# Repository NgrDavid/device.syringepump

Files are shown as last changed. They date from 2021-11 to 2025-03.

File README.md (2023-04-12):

## Harp Syringe Pump
This is a repository for the Harp Syringe Pump. The Harp Syringe Pump is a device that can be used to control the flow of liquid through a syringe by driving a stepper motor.
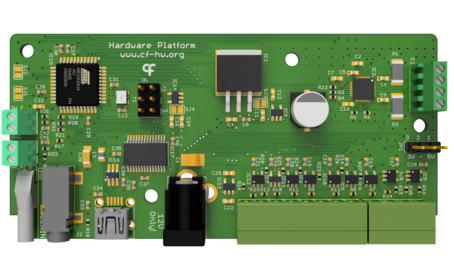
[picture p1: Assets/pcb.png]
HarpSyringePump


### Key Features ###

* Low and High-level interface control of the stepper motor
* General digital inputs configurable to trigger hardware events
* Digital outputs configurable to report hardware events
* Includes on-board stepper-motor driver
* Included mechanical designs and assembly instructions

### Connectivity ###

* 1x clock sync input (CLKIN) [stereo jack]
* 1x USB (for computer) [USB type B]
* 1x 12V supply [barrel connector jack]
* General purpose I/O (5V) [screw terminal]

## Interface ##

The interface with the Harp Behavior can be done through [Bonsai](https://bonsai-rx.org/) or a dedicated GUI (Graphical User Interface).

## Licensing ##

Each subdirectory will contain a license or, possibly, a set of licenses if it involves both hardware and software.

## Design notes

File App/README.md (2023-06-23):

# Syringe Pump GUI

This repository folder contains the Syringe Pump GUI (henceforth GUI) application that allows to configure the Syringe Pump device, developed by the Scientific Hardware Platform at the Champalimaud Foundation.

The Syringe Pump device is a Harp device and has all the inherent functionality of Harp devices.

The GUI was developed using [.NET 6](https://dotnet.microsoft.com/), [Avalonia](https://avaloniaui.net/) with ReactiveUI and makes direct use of the [Bonsai.Harp](https://github.com/bonsai-rx/harp) library.

As with other Harp devices, the Syringe Pump can also be used in [Bonsai](bonsai-rx.org/) using the [Bonsai.Harp.CF](https://github.com/bonsai-rx/harp.cf) package. 

## Installation

Go to the Releases page to download the latest version for your Operating System.

Currently there are x64 builds for Windows and Linux. Mac builds will be available in the future.

Portable builds are also available.

### Linux

Since the application accesses the serial port, your user needs to be on the `dialout`group or equivalent.

There might be other alternatives to this, but at least on Ubuntu and Fedora que command that you need to run to add your user to the `dialout` group is:

```sh
sudo usermod -a -G dialout <USERNAME>
```

## For developers

### Build Windows installer using NSIS manually

- Install NSIS 3 on your Windows machine
- Build and publish the application using the .NET 6 SDK command-line tools
  ```
    dotnet publish -r win-x64 /p:PublishSingleFile=false /p:IncludeNativeLibrariesInSingleFile=true /p:Configuration=Release
  ```
- Run makesis to generate the installer
    ```
     makensis.exe /DVERSION_MAJOR=0 /DVERSION_MINOR=1 /DVERSION_BUILD=0 .\SyringePump.nsi
    ```
- The installer will be available at `.\bin\Release\net6.0\win-x64\SyringePump.vx.x.x-win-x64.self-contained.exe`

### Build .app image for macOS

The project uses dotnet-bundle (https://github.com/egramtel/dotnet-bundle) to generate a .app image for macOS.

To build the .app image, run the following commands on the solution folder:

```sh
dotnet restore -r osx-x64 -p:TargetFramework=net6.0
dotnet msbuild -t:BundleApp -p:RuntimeIdentifier=osx-x64 -property:Configuration=Release -p:UseAppHost=true -p:TargetFramework=net6.0
```

### Build tar.gz package for Linux (either in Linux or WSL)

To build the tar.gz package, run the following commands on the solution folder:

First you need to make sure that the [`dotnet-packaging`](https://github.com/quamotion/dotnet-packaging) tool is installed

Run the following commands to install the tool:

```sh
dotnet tool install --global dotnet-tarball
```

Then run the following commands to build the tar.gz package:

```sh
dotnet restore -r linux-x64 -p:TargetFramework=net6.0
dotnet msbuild -p:RuntimeIdentifier=linux-x64 -property:Configuration=Release -p:UseAppHost=true -p:TargetFramework=net6.0 /t:CreateTarball
```

## Roadmap

See the [open issues](https://github.com/harp-tech/device.syringepump/issues) for a list of proposed features (and known issues).

## Contributing

Contributions are what make the open source community such an amazing place to be learn, inspire, and create. Any contributions you make are **greatly appreciated**.

1. Fork the Project
2. Create your Feature Branch (`git checkout -b feature/AmazingFeature`)
3. Commit your Changes (`git commit -m 'Add some AmazingFeature'`)
4. Push to the Branch (`git push origin feature/AmazingFeature`)
5. Open a Pull Request

## Authors

Hardware & Software Platform of the Champalimaud Foundation.

### Main contributors

- Artur Silva
- Luís Teixeira

## License

See `LICENSE` file for more information.

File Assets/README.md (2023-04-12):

### Licensing
Copyright harp-tech 2023

<br />This work is licensed under a <a rel="license" href="http://creativecommons.org/licenses/by/4.0/">Creative Commons Attribution 4.0 International License</a>.

#### You are free to:
*Share* — copy and redistribute the material in any medium or format.

*Adapt* — remix, transform, and build upon the material for any purpose, even commercially.

#### Under the following terms:
*Attribution* — You must give appropriate credit, provide a link to the license, and indicate if changes were made. You may do so in any reasonable manner, but not in any way that suggests the licensor endorses you or your use.

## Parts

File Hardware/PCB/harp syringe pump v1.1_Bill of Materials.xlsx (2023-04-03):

Part(s) | Quantity Low Level | Quantity Full | Description | Distributor | Part. No.
IC1 | 1 | 1 | Reguladores de tensão linear 3-TERMINAL POS REG 5V 1A | Mouser | 926-LM340S-5.0/NOPB | Low Level Only Bold
IC2 | 1 | 1 | DMOS Microstepping Driver with Translator and Overcurrent Protection IC | Farnell | 2057418
IC3, IC13, IC14 | 0 | 3 | LDO 250mA Ultra-Lo Noise LDO Reg | Mouser | 595-LP5907MFX-3.3NPB
IC4, IC5, IC6, IC7, IC10, IC11, IC12 | 0 | 7 | SingleBuffer / Driver, 1.65V to 5.5V, SOT-23-5 | Mouser | 595-SN74LVC1G125DBVR
IC8, IC9 | 0 | 2 | Buffers e line drivers 1.65-5.5V Single Non-Inverting TTL | Mouser | 863-M74VHC1GT50DTT1G
IC15 | 0 | 1 | Microcontroladores de 8 bits - MCU 44TQFP, IND TEMP GREEN, 1.6-3.6V | Mouser | 556-ATXMEGA128A4U-AU
IC16 | 0 | 1 | ESD Protection Low Cap | Mouser | 511-USBLC6-2SC6Y
IC17 | 0 | 1 | IC USB USB to Serial UART Enhanced IC SSOP-28 | Mouser | 895-FT232RL
C35, C36 | 0 | 2 | CAP CER 47pF 50V ±5% C0G 0402 | Mouser | 77-VJ0402A470JXACBC
C33 | 0 | 1 | CAP CER 4.7nF 100V ±10% X7R 0402 | Mouser | 81-GRM155R72A472KA01
C13, C14, C15, C16, C17, C18, C19, C20, C21, C22, C27, C28, C29, C34, C37, C39, C40, C41, C42 | 2 | 19 | CAP CER 100nF 10V ±10% X5R 0402 | Farnell | 2310530
C2, C5, C8 | 3 | 3 | CAP CER 100nF 100V ±10% X7R 0402 | Mouser | 81-GRM188R72A104KA35
C4, C7, C10 | 3 | 3 | CAP CER 220nF 100V ±10% X7R 0603 | Mouser | 81-GCM188R71H224KA4J
C30, C31 | 0 | 2 | CAP CER 330nF 10V ±10% X5R 0402 | Digikey | CL05A334KP5NNNC
C6, C9 | 2 | 2 | CAP CER 1uF 25V ±20% X5R 0603 | Mouser | 581-06033D105K
C38 | 0 | 1 | CAP TAN 4.7uF 10V ±10% 1206 | Mouser | 80-T491A475K107280
C11, C12, C23, C24, C25, C26, C32 | 1 | 7 | CAP CER 10uF 35V ±20% X5R 0603 | Mouser | 81-GRM188R6YA106MA3D
C1 | 1 | 1 | CAP TAN 22uF 20V ±10% 1210 | Mouser | 667-20TQC22MYFB
C3 | 1 | 1 | CAP ELE 100uF 25V ±20% | Mouser | 667-EEE-FK1E101P
R1, R2 | 2 | 2 | RES SMD 0.1Ω 1% 2010 1W | Mouser | 652-CRM2010FXR100ELF
R15, R16, R30, R31 | 2 | 4 | RES SMD 33Ω ±5% 0402 | Mouser | 667-ERJ-2GEJ330X
R34, R35 | 2 | 0 | RES SMD 33Ω ±5% 0402 | Mouser | 667-ERJ-2GEJ330X
R17 | 0 | 1 | RES SMD 68Ω 5% 0402 | Mouser | 71-CRCW0402-68-E3
R23, R24, R25, R26, R27, R28 | 6 | 0 | RES SMD 1kΩ 1% 0402 | Mouser | 667-ERJ-2RKF1001X
R19, R20, R21 | 0 | 3 | RES SMD 10kΩ 1% 0402 | Mouser | 667-ERJ-2RKF1002X
R32, R33 | 2 | 0 | RES SMD 10kΩ 1% 0402 | Mouser | 667-ERJ-2RKF1002X
R3 | 1 | 1 | RES SMD 24.9kΩ 1% 0402 | Mouser | 667-ERJ-2RKF2492X
R6 | 0 | 1 | RES SMD 39kΩ 1% 0402 | Mouser | 667-ERJ-2RKF3902X
R6 | 1 | 0 | RES SMD 36kΩ 1% 0402 | Mouser | 667-ERJ-2RKF3602X
R5 | 0 | 1 | RES SMD 54.9kΩ 1% 0402 | Mouser | 667-ERJ-U02F5492X
R5 | 1 | 0 | RES SMD 95.3kΩ 1% 0402 | Mouser | ERJ-U02F9532X
R4, R7, R8, R9, R10, R11, R12, R14, R22, R29 | 2 | 10 | RES SMD 100kΩ ±1% 0402 | Mouser | 667-ERJ-2RKF1003X
R18 | 0 | 1 | RES SMD 1MΩ 1% 0402 | Mouser | 652-CR0402FX-1004GLF
LED1 | 0 | 1 | LED, Green, 1.6mm x 0.8mm, 566 nm, 2.1 V, 20 mA, 15 mcd | Mouser | 78-TLMP1100-GS08
SW1 | 0 | 1 | Interruptores táteis 2.45N OF Long Stroke Green Button | Mouser | 653-B3AL-1001P
SW2 | 0 | 1 | Interruptores táteis 1.96N OF Long Stroke Red Button | Mouser | 653-B3AL-1000P
Y1 | 0 | 1 | 32MHz 10ppm | Mouser | 998-1001CI5032.0000T
J2 | 0 | 1 | SMT 3.5 STEREO REEL | Mouser | 502-35RASMT2BHNTRX
L1 | 0 | 1 | 40ohms 100MHz 1.5A Monolithic 0805 SMD | Mouser | 875-MI0805K400R-10
J3 | 0 | 1 | 6P DR UNSHRD HRD | Mouser | 649-67996-206HLF
X4 | 0 | 1 | UX60-MB-5S8 | Mouser | 798-UX60-MB-5S8
USB Cable | 0 | 1 | USB A - MINI-B 0.8M - MINI-B 0.8M BLACK | Mouser | 538-88732-8502
 | 0 | 1 | Tubos de Luz LED CML LIGHTPIPE | Mouser | 606-7513D2-L
JP1 | 0 | 1 | 3POS HDR 15AU | Mouser | 649-68001-203HLF
 | 0 | 1 | Distribuidores e Alojamento de Fios JUMPER SKT BLACK OPEN TOP | Mouser | 855-M7582-46
J1 | 1 | 1 | CC PCB 2.1MM | Mouser | 163-179PH-EX
SW_LIMITERS | 2 | 2 | SWITCH SNAP ACT SPST-NC 5A 125V | Mouser | 653-SS5GL22T
WALL ADAPTER | 1 | 1 | AC/DC Power Supply, Class II, Fixed, 1 Output, 90 V, 264 V, 12 W, 12 V | Farnell | VEL12US120-EU-JA
X1 | 1 | 1 | Wire-To-Board Terminal Block, 2.54 mm, 4 Ways, 30 AWG, 16 AWG, 1.4 mm², Screw | Farnell | 282834-4
 | 1 | 1 | 20.1550M/4-E - Pluggable Terminal Block, 3.5 mm, 4 Ways | Farnell | 2575217
 | 1 | 1 | 20.1550M/8-E - Pluggable Terminal Block, 3.5 mm, 8 Ways | Farnell | 2575220
X3 | 1 | 1 | Horizontal, Header, 3.5 mm, 4 Ways, 10 A, 250 V, Through Hole Right Angle | Farnell | 20.155MH/4-E
X2 | 1 | 1 | Horizontal, Header, 3.5 mm, 8 Ways, 10 A, 250 V, Through Hole Right Angle | Farnell | 20.155MH/8-E
 | 1 | 1 | Heat Sink, Black Anodised, 87 °C/W, For DIP, PLCC, SMD, 4.8mm/6.3mm/8mm | Farnell | 4302175
 | 1 | 1 | Thermal Conductive Foil, 0.37 W/m.K | Farnell | 1211706
 | 2 | 2 | Blocos de terminais fixos 2P SIDE ENTRY 2.54mm | Mouser | 571-282834-2
SJ1, SJ2, SJ3, SJ4 | 4 | 4 | - | - | -
Components | 51 | 112
PCB |  |  | 100mmx48mm 5x 2layers 35um
Licensed under the TAPR Open Hardware License (www.tapr.org/OHL)
Copyright 2020 Artur Silva, Champalimaud Foundation Scientific Hardware Platform

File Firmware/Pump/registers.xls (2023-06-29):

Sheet: registers
Has event. | When | Type | Array | Array Len. | Register Name | Description | Mask Type | Value | Name | Desciption
no |  | U8 | no |  | ENABLE_MOTOR_DRIVER | Enable the motor driver | bit | (1<<0) | MOTOR_ENABLE | Enable motor when equal to 1
no |  | U8 | no |  | START_PROTOCOL | Enable the defined protocol | bit | (1<<0) | START_PROTOCOL | Start the protocol when equal to 1
yes | Yes, when the register changes (either edge STEP changes) | U8 | no |  | STEP_STATE | Control the step of the motor controller | bit | (1<<0) | STEP_PIN | Status of the STEP motor controller pin
yes | Yes, when the register changes (either edge DIR changes) | U8 | no |  | DIR_STATE | Control the direction of the motor controller | bit | (1<<1) | DIR_PIN | Status of the DIR motor controller pin
yes | Yes, when the register changes (switch is triggered/cleared) | U8 | no |  | SW_FORWARD_STATE | State of the forward switch limit | bit | (1<<0) | SW_F_PIN | Status of the forward switch limit
yes | Yes, when the register changes (switch is triggered/cleared) | U8 | no |  | SW_REVERSE_STATE | State of the reverse switch limit | bit | (1<<1) | SW_R_PIN | Status of the reverse switch limit
yes | Everytime the pin changes the state | U8 | no |  | INPUT_STATE | Value of input 0 pin | bit | (1<<0) | DI0 | Input 0 value
no |  | U8 | no |  | SET_DOS | Set digital outputs | bit | (1<<0) | SET_DO0 | Write one to this bit will put digital out 0 into High state
 |  |  |  |  |  |  | bit | (1<<1) | SET_DO1 | Write one to this bit will put digital out 1 into High state
no |  | U8 | no |  | CLEAR_DOS | Clear digital outputs | bit | (1<<0) | CLR_DO0 | Write one to this bit will put digital out 0 into Low state
 |  |  |  |  |  |  | bit | (1<<1) | CLR_DO1 | Write one to this bit will put digital out 1 into Low state
no |  | U8 | no |  | DO0_CONFIG | Configures which signal is connected to the digital output 0 | mask | (3<<0) | OUT0_CONF | Select OUT0 function
 |  |  |  |  |  |  | group_mask | (0<<0) | OUT0_SOFTWARE | Digital output controlled by software
 |  |  |  |  |  |  | group_mask | (1<<0) | OUT0_SWLIMIT | Either limits reached (register SW_FORWARD_STATE OR SW_REVERSE_STATE)
no |  | U8 | no |  | DO1_CONFIG | Configures which signal is connected to the digital output 1 | mask | (3<<0) | OUT1_CONF | Select OUT1 function
 |  |  |  |  |  |  | group_mask | (0<<0) | OUT1_SOFTWARE | Digital output controlled by software (SET_DO1 and CLEAR_DO1)
 |  |  |  |  |  |  | group_mask | (1<<0) | OUT1_DATA_SEC | Toggles each second when is acquiring
 |  |  |  |  |  |  | group_mask | (2<<0) | OUT1_STEP_STATE | Equal to register STEP_STATE
no |  | U8 | no |  | DI0_CONFIG | Configuration of the digital input 0 (DI0) | mask | (3<<0) | DI0_CONF | Select IN0 function
 |  |  |  |  |  |  | group_mask | (0<<0) | DI0_SYNC | Use as a pure digital input
 |  |  |  |  |  |  | group_mask | (1<<0) | DI0_RISE_FALL_UPDATE_STEP | Update STEP with a rising edge
 |  |  |  |  |  |  | group_mask | (2<<0) | DI0_RISE_START_PROTOCOL | Will trigger the predefined protocol on a rising edge
no |  | U8 | no |  | MOTOR_MICROSTEP | Defines the motor microstep | mask | (7<<0) | MICROSTEP
 |  |  |  |  |  |  | group_mask | (0<<0) | STEP_FULL | Full step (2 phase)
 |  |  |  |  |  |  | group_mask | (1<<0) | STEP_HALF | Half step
 |  |  |  |  |  |  | group_mask | (2<<0) | STEP_QUARTER | Quarter step
 |  |  |  |  |  |  | group_mask | (3<<0) | STEP_EIGHTH | Eighth step
 |  |  |  |  |  |  | group_mask | (4<<0) | STEP_SIXTEENTH | Sixteenth step
no |  | U16 | no |  | PROTOCOL_NUMBER_STEPS | Number of steps [1;65535]
no |  | FLOAT | no |  | PROTOCOL_FLOWRATE | Flowrate value in uL/s ]0;max_float[
no |  | U16 | no |  | PROTOCOL_PERIOD | Period for each step in ms [1;65535]
no |  | FLOAT | no |  | PROTOCOL_VOLUME | Volume value in uL ]0;max_float[
no |  | U8 | no |  | PROTOCOL_TYPE | Step-based (0) or Volume-based protocol (1)
no |  | U8 | no |  | CALIBRATION_VALUE_1 | Calibration value 1
no |  | U8 | no |  | CALIBRATION_VALUE_2 | Calibration value 2
no |  | U8 | no |  | EVT_ENABLE | Enable the Events | bit | (1<<0) | EVT_STEP_STATE | Event of register STEP_STATE
 |  |  |  |  |  |  | bit | (1<<1) | EVT_DIR_STATE | Event of register DIR_STATE
 |  |  |  |  |  |  | bit | (1<<2) | EVT_SW_FORWARD_STATE | Event of register SW_FORWARD_STATE
 |  |  |  |  |  |  | bit | (1<<3) | EVT_SW_REVERSE_STATE | Event of register SW_REVERSE_STATE
 |  |  |  |  |  |  | bit | (1<<4) | EVT_INPUT_STATE | Event of register INPUT_STATE
 |  |  |  |  |  |  | bit | (1<<5) | EVT_PROTOCOL_STATE | Event of register PROTOCOL_STATE
no |  | U8 | no |  | SET_BOARD_TYPE | Type of the board | mask | (3<<0) | BOARD_TYPE
 |  |  |  |  |  |  | group_mask | (0<<0) | PUMP
 |  |  |  |  |  |  | group_mask | (1<<0) | FISH_FEEDER
 |  |  |  |  |  |  | group_mask | (2<<0) | STEP_MOTOR
yes | Yes, when the register changes (either edge PROTOCOL changes) | U8 | no |  | PROTOCOL_STATE | State of the protocol (running or stopped) | bit | (1<<0) | PROTOCOL_STATE | Status of the Protocol
no |  | U8 | no |  | PROTOCOL_DIRECTION | Protocol direction

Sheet: meta data
who am I: | 1280
firmware major version: | 1
firmware minor version: | 0
hardware major version: | 1
hardware minor version: | 0
assembly version: | 0
device name: | Pump

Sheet: ios
Pin Name | PORT | Pin | Direction | Use Input | Out | Out default | Pull | Sense | Int. priority | Int. number | Desciption | Neg. Output
STEP | PORTA | 0 | output | yes | digital | 0 |  |  |  |  | Motor controller input step | no
DIR | PORTA | 1 | output | yes | digital | 0 |  |  |  |  | Motor controller direction input | no
MS1 | PORTA | 2 | output | no | digital | 0 |  |  |  |  | Motor configuration bit 1 | no
MS2 | PORTA | 3 | output | no | digital | 0 |  |  |  |  | Motor configuration bit 2 | no
MS3 | PORTA | 4 | output | no | digital | 0 |  |  |  |  | Motor configuration bit 3 | no
EN_DRIVER | PORTA | 5 | output | yes | digital | 1 |  |  |  |  | Motor controller enable | yes
SLEEP | PORTA | 6 | output | no | digital | 1 |  |  |  |  | Motor controller sleep | yes
RESET | PORTA | 7 | output | no | digital | 1 |  |  |  |  | Motor controller reset | yes
IN00 | PORTB | 0 | input |  |  |  | tristate | both_edges | low | 0 | Board digital input 0
OUT00 | PORTB | 1 | output | yes | digital | 0 |  |  |  |  | Board digital output 0 | no
OUT01 | PORTB | 2 | output | yes | digital | 0 |  |  |  |  | Board digital output 1 | no
BUF_EN | PORTB | 3 | output | no | digital | 1 |  |  |  |  | Enable signal for user controller inputs | yes
TYPE0 | PORTC | 0 | input |  |  |  | down | both_edges | low | 0 | Board type pin 0
TYPE1 | PORTC | 1 | input |  |  |  | down | both_edges | low | 0 | Board type pin 1. If pin 0 == 1 -> FISH_FEEDER. If both are 0 == pump. If pin 1 == 1 STEP_MOTOR
SW_F | PORTC | 4 | input |  |  |  | up | both_edges | low | 0 | Limit switch signal (forward)
SW_R | PORTC | 5 | input |  |  |  | up | both_edges | low | 0 | Limit switch signal (reverse)
EN_DRIVER_UC | PORTD | 0 | input |  |  |  | tristate | both_edges | low | 0 | Enable driver from user output
BUT_PUSH | PORTD | 5 | input |  |  |  | up | both_edges | low | 0 | Button to push syringe
BUT_PULL | PORTD | 6 | input |  |  |  | up | both_edges | low | 0 | Button to pull syringe
BUT_RESET | PORTD | 7 | input |  |  |  | up | both_edges | low | 0 | Button to reset to initial state

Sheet: options
Array | Type | Array | Bits type | Direction | Use input | Pull | Sense | Int. priority | Int. number | Int. Mask | Out | Neg. Output
 |  |  |  | input | yes | up | both_edges | low | 0 |  | digital | yes
yes | U8 | yes | bit | output | no | down | rising_edge | med | 1 |  | wire_or | no
no | U16 | no | mask |  |  | tristate | falling_edge | high |  |  | wire_and
 | U32 |  | group_mask |  |  | busholder | low_level | off |  |  | wired_or_pull
 | U64 |  |  |  |  |  | no_interrupt |  |  |  | wired_and_pull
 | I8
 | I16
 | I32
 | I64
 | FLOAT

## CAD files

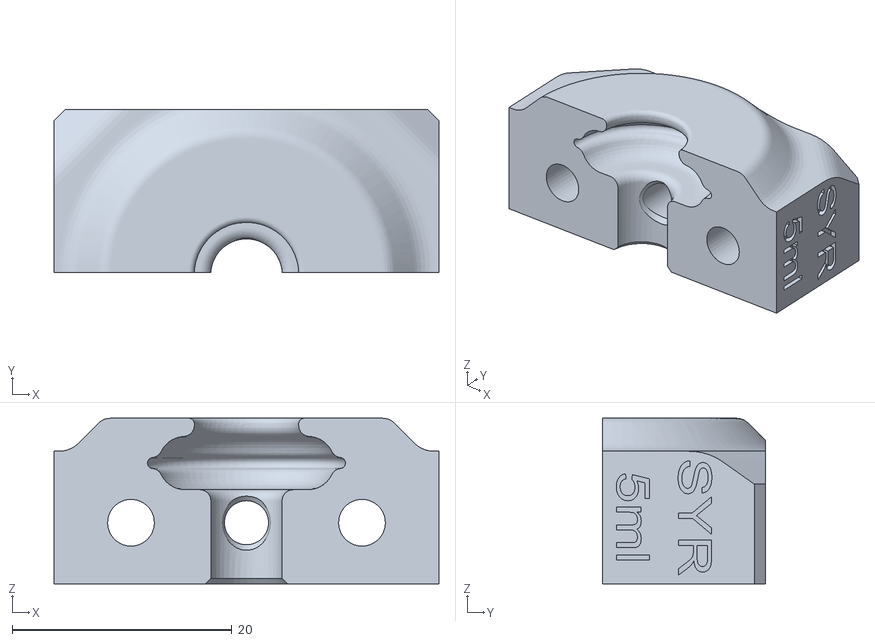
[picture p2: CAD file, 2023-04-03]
Hardware/Mechanical/33_SHPHamilton_SYR_5ml_SYP_BLOCK_HOLDER-B.STL
35.0 x 14.8 x 15.1

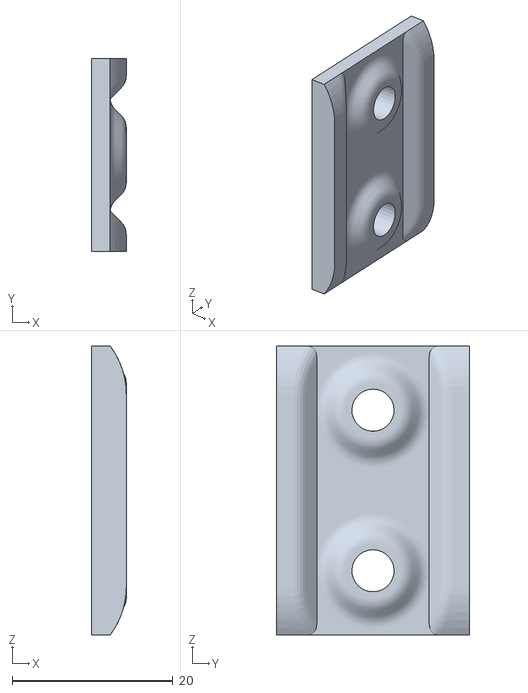
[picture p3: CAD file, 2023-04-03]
Hardware/Mechanical/20_1_x2_SHPSyPump_SideSlider_v2_4-3_mm_to_order.STL
4.30 x 24.0 x 36.0

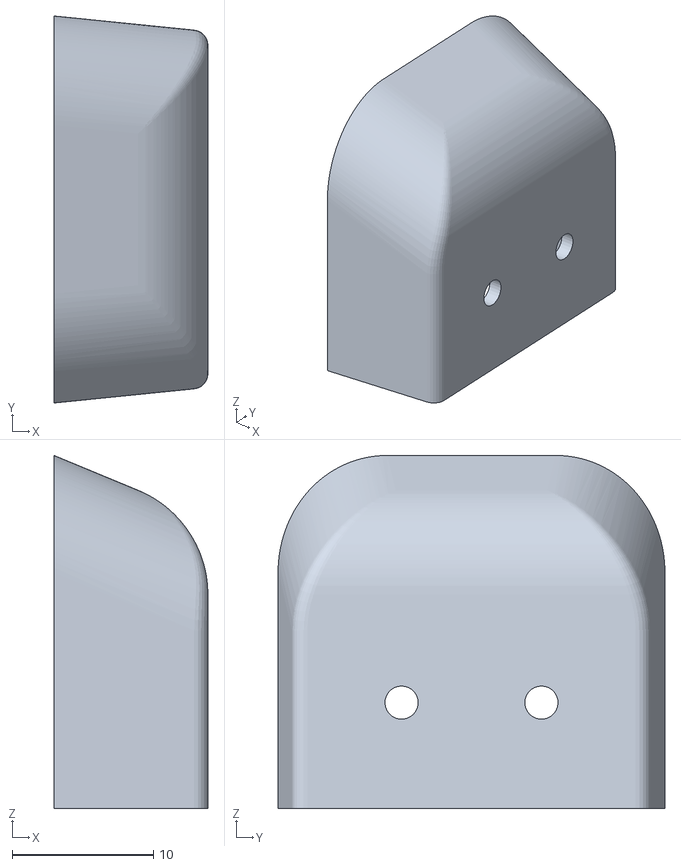
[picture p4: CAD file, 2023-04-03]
Hardware/Mechanical/27_x2_SHPBase_End_Switch-2.STL
10.9 x 27.4 x 25.0

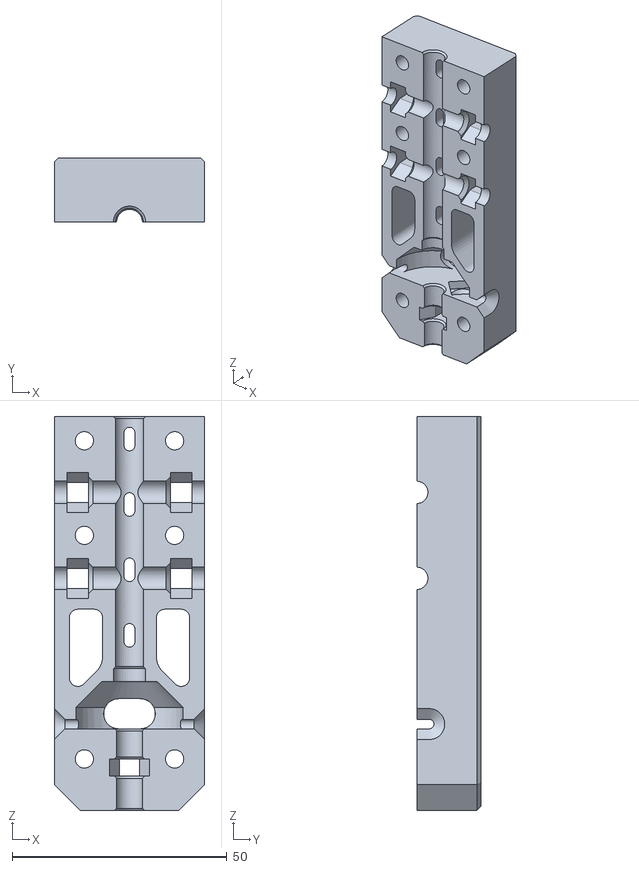
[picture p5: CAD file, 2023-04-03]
Hardware/Mechanical/6_SHPSyPump_M5_Pusher_Split_Block_Multifit_Matrix_Seringa_12ml-B2.STL
35.0 x 15.0 x 91.7

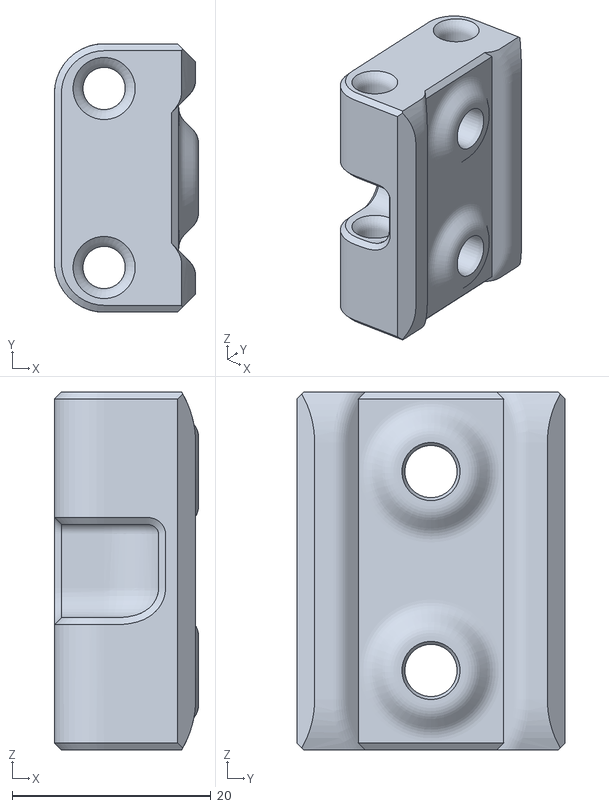
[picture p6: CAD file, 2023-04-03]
Hardware/Mechanical/24_SHP_SyPump_Switch_SideSlider_v1e2_ONE_PIECE_LEVERLESS_VERSION.STL
14.5 x 27.0 x 36.0

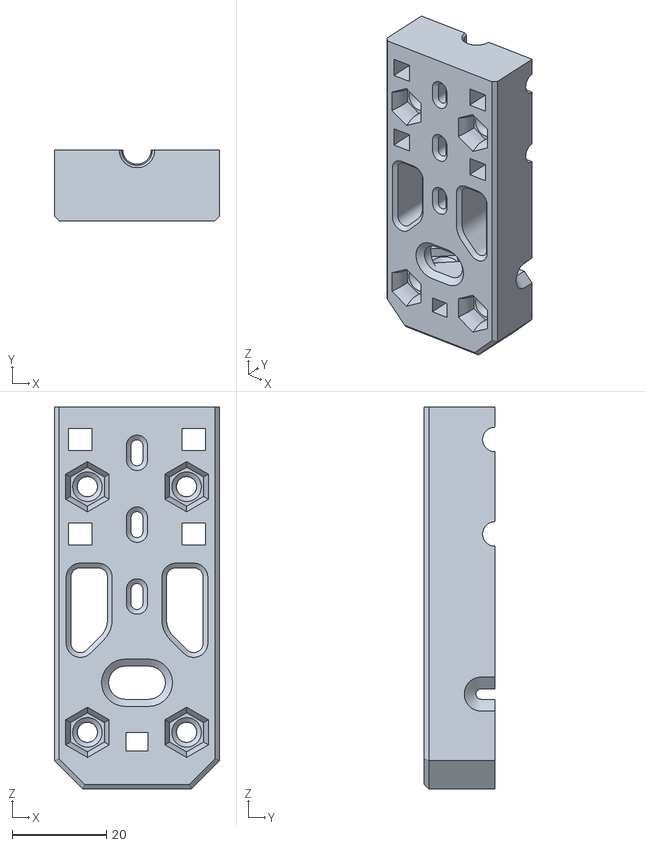
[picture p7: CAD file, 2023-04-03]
Hardware/Mechanical/5_SHPSyPump_M5_Pusher_Split_Block_Multifit_Matrix_Seringa_12ml-A2.STL
35.0 x 15.0 x 80.9

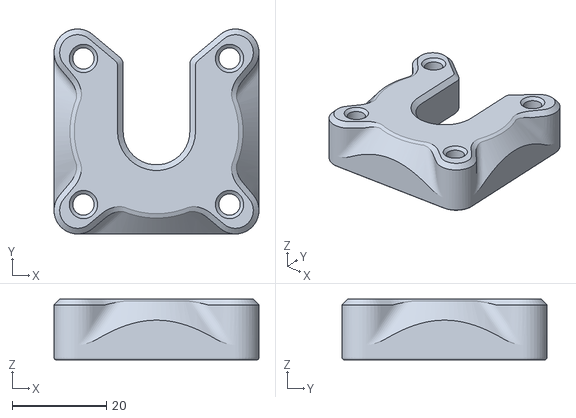
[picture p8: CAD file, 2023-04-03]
Hardware/Mechanical/18_SHPSyPumo_Locker_Plate_to_6ml_Plastic_Syringe.STL
43.5 x 43.5 x 12.9

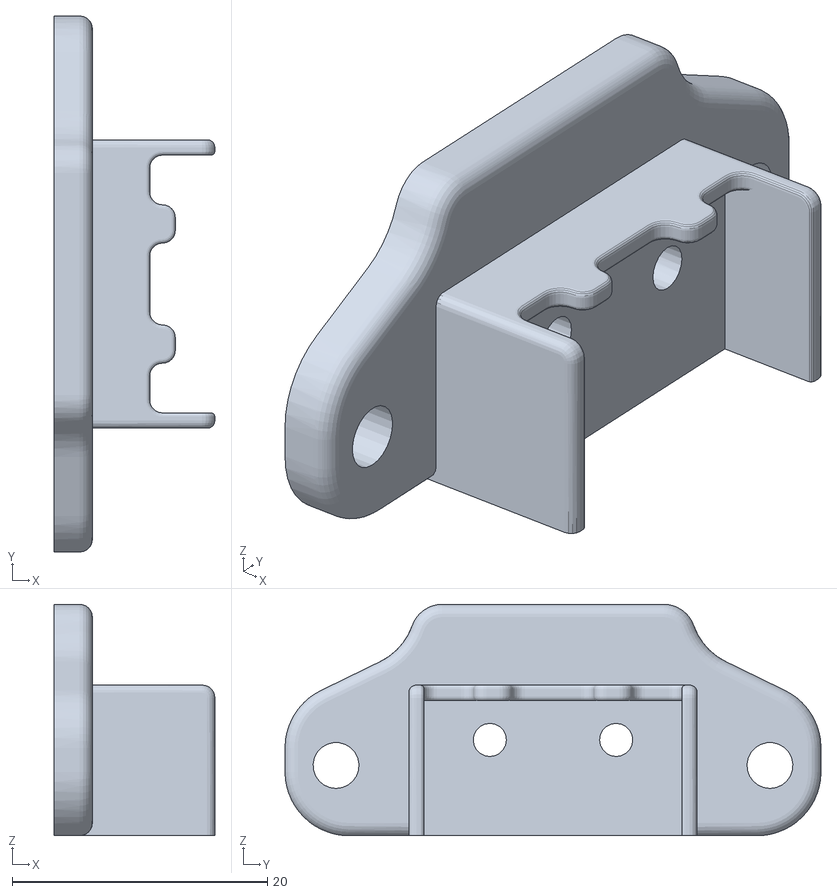
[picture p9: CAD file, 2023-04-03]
Hardware/Mechanical/29_x2_SHPBase_End_Switch-1.STL
12.6 x 42.0 x 18.1

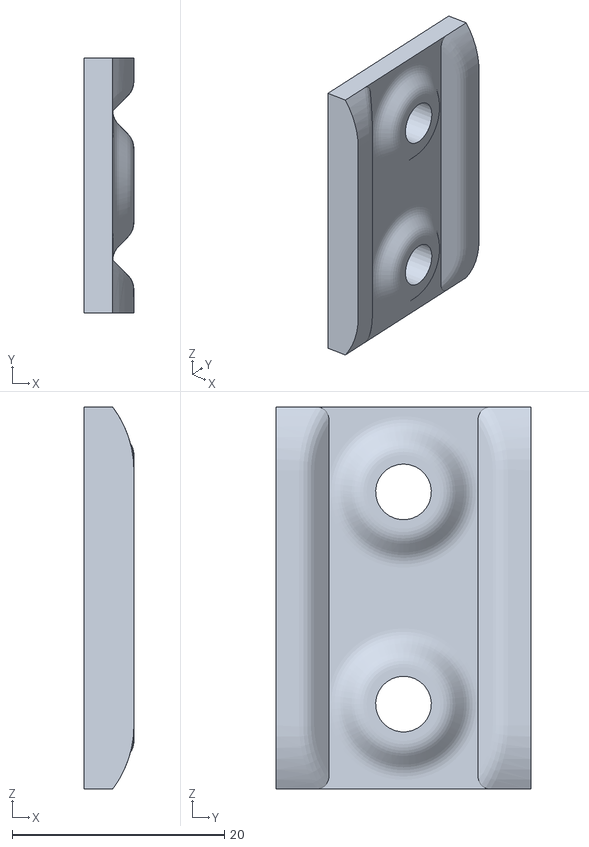
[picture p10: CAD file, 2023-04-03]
Hardware/Mechanical/20_3_x2_SHPSyPump_SideSlider_v2_4-7_mm_to_order.STL
4.70 x 24.0 x 36.0

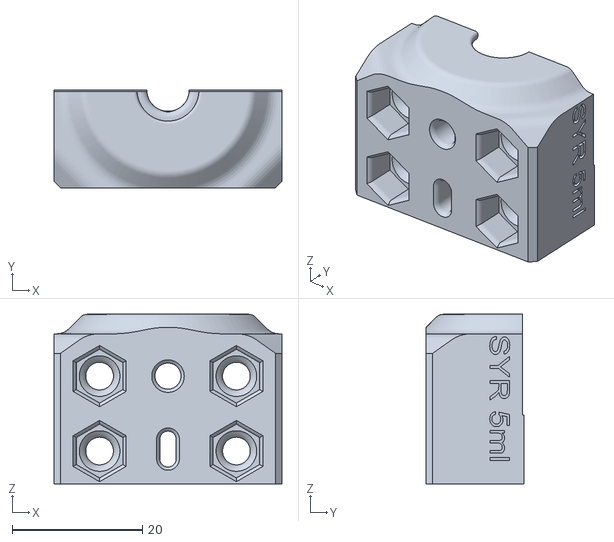
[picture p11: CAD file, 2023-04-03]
Hardware/Mechanical/15_SHPHamilton_SYR_5ml_SYP_BLOCK_HOLDER-A.STL
35.0 x 15.0 x 26.0

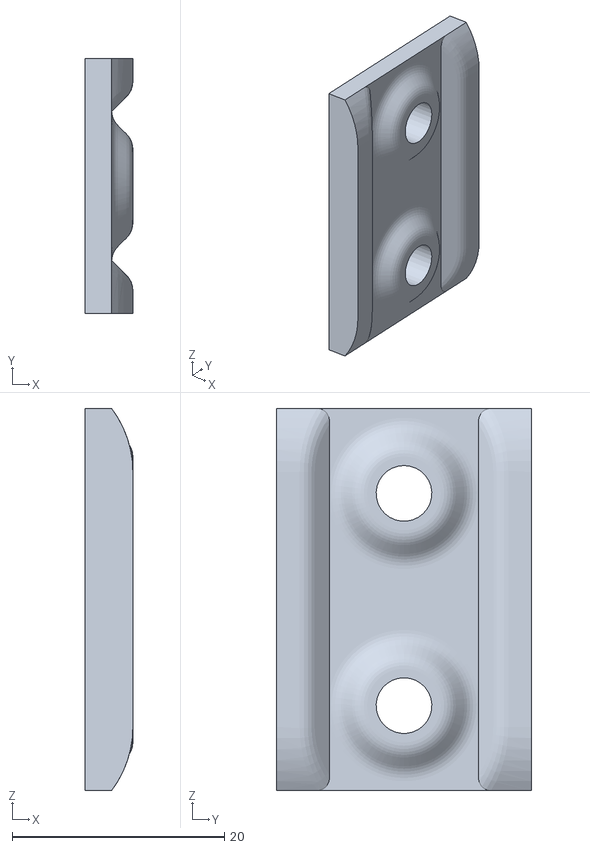
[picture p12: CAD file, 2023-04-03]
Hardware/Mechanical/20_2_x2_SHPSyPump_SideSlider_v2_4-5_mm_to_order.STL
4.50 x 24.0 x 36.0

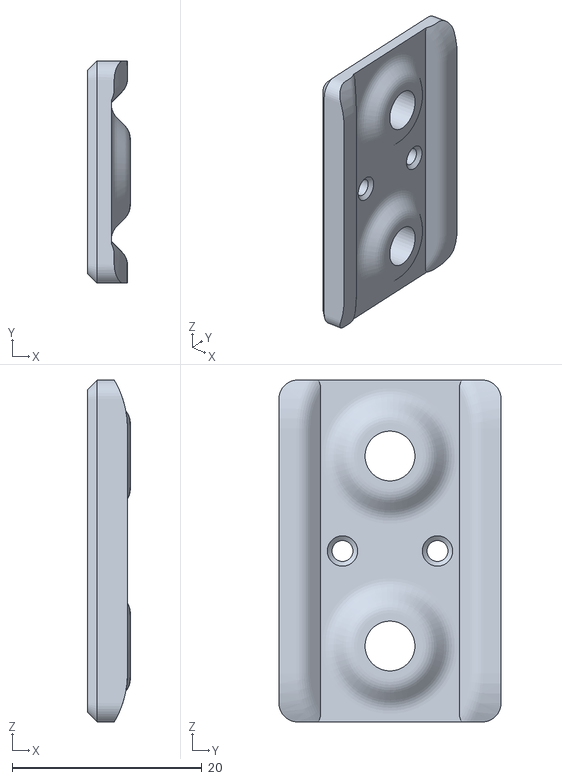
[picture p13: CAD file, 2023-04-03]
Hardware/Mechanical/22_SHPSyPump_Switch_SideSlider_v2-1_Oposite.STL
4.50 x 23.4 x 36.0

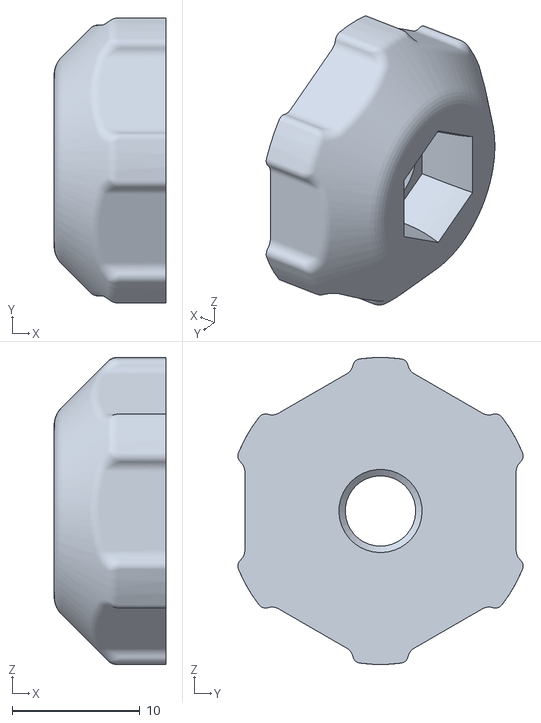
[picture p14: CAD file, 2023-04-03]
Hardware/Mechanical/7_SHP_SyP_Tensioner_Nut_M5_Pulling_IN_Force.STL
8.75 x 22.3 x 24.0

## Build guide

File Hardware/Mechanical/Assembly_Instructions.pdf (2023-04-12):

Assembly instructions

Note: Exploded view with the identification number of each one of the parts is available here.

1. Laser | cut | the | parts | available | in | the | repository. | For | the
SHPSP_Frame_PC_V1_HAMILTON_SYR_10ml_drawing_GB_LR_5mm.pdf file a 5mm
acrylic | | sheet | must | be | used, | | while | for | the
SHPSP_Frame_PC_V1_HAMILTON_SYR_10ml_drawing_GB_LR_3mm.pdf a 3mm acrylic sheet must be used.

2. Assemble all the acrylic parts of the main body (1) (all the acrylic parts, except the cover) without gluing as depicted in the figures below (remove the acrylic protective cover prior to assembling).

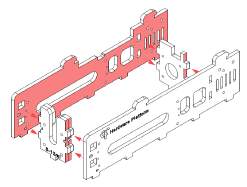
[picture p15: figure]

3. In order to ensure a more robust gluing and minimize the effects ot the acrylic tolerances, prior to gluing ensure that:
a. Squeeze gently the side wall inwards and press the inside parts outwards
b. Make sure that the main walls are parallel to each other. Check that the walls are in line with the markers of the bottom acrylic.

4. Using a brush, apply acrylic glue to the assembled structure.
Note: It is recommended that the gluing should be done on top of a glass to avoid that any spills might damage the desk)
a. Apply a thin layer of of glue on the back wall with one hand, while holding the assembled structure with the other hand;

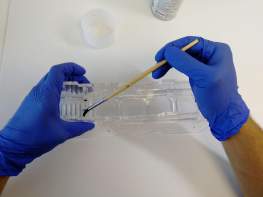
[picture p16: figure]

b. Repeat the same procedure for the front wall with one hand, while holding the assembled structure with the other hand;
c. Apply a thin layer of glue on the lateral walls while making sure that those walls are in line with the markers of the bottom acrylic, i.e., parallel to each other. You can slightly move the acrylic walls to make sure they are glued as parallel as possible.
Note: You can use a ruler to help in this procedure

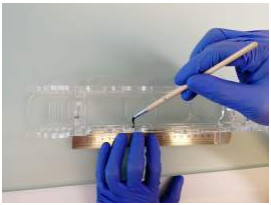
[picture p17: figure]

d. Apply glue to all of the structure edges to make sure the acrylic parts are bonded to each other. Turn the structure upside down and glue the bottom edges.
5. 3D print the STL files available in the repository, namely:
- 1x 3D Printed Split Block Bottom (5)
- 1x 3D Printed Split Block Top (6)
- 1x 3D Printed Lock Tight Nut (7)
- 1x 3D Printed Syringe Block Holder Top (15)
- 2x 3D Printed Side Slider (20)
- 1x 3D Printed Slider - non-Switch Side (22)
- 1x 3D Printed Slide Block (24)
- 2x 3D Printed End Switch Cover (27)
- 2x 3D Printed End Switch Base (29)
- 1x 3D Printed Syringe Block Holder Bottom (33)
6. Glue with super glue (Loctite 401 for example) the nuts to the printed parts. For each nut, use a correspondent screw to pull the nut towards the part in order to make sure it is properly attached to it
a. Glue the the brass hex nut M5 (8) to part (7)

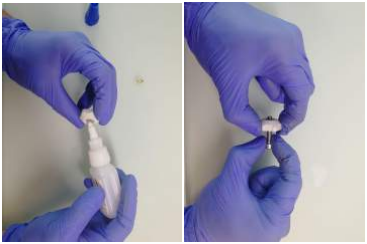
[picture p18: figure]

b. Glue a M4 square steel nut (10) to part (6)

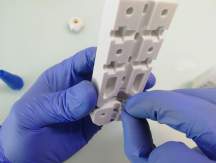
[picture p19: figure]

c. Glue a M4 square steel nut (10) to part (5)

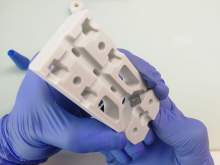
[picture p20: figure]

d. Glue 4x M4 hex nuts (12) to part (5)

e. Glue 2x M4 hex nuts (12) and 2x M4x25mm hex screws (17) to part (33)

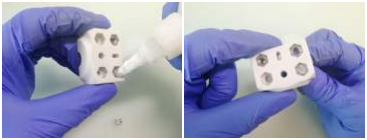
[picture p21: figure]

f. Glue 4x M4x25mm hex screw (17) to the main acrylic body. Place the 3D printed part while gluing the screws to align the screws

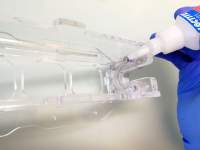
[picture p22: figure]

g. Glue 2x M2.5 hex nuts to part (29) for each one of the 3D switch base

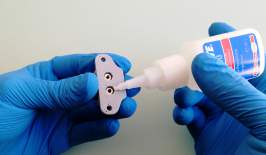
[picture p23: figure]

7. Insert the backlash nut and a brass nut (8) into the M5 rod (9)

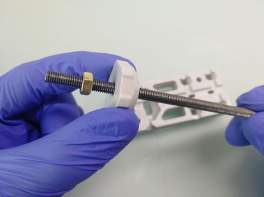
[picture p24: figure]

8. Place the rod with the nuts and place 4x M5 lock nuts (19). Before placing the top part, make sure that the backlash nut is loose, i.e, the rod rotates freely and the nut is not pressed against the printed part. Attach the top part and screw with the 4x M4x25mm hex socket cap screw (11)

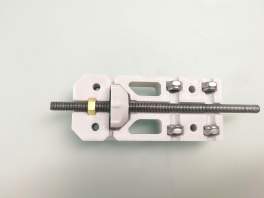
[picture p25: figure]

9. With a screwdriver inserted in the bottom hole, tighten the nut by pressing downwards until the rod cannot move completely and no backlash is felt.
Attach the 2x M4x16mm hex socket cap screw (14) and tight the screw until you can feel that the rod is starting to rotate freely.

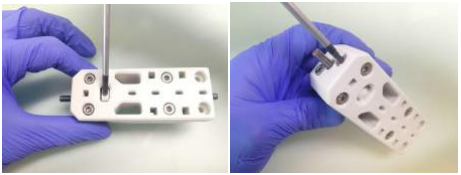
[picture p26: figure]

10. Screw and glue thumb nuts (16) on the edge of the M4 rods (25)

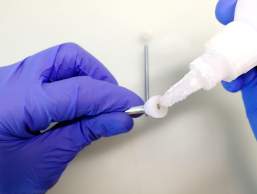
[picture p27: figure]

11. Insert the rods on the part (24) while placing a thumb nub (16) in the middle and on the opposite edge

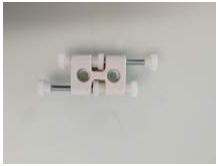
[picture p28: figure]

12. Attach the motor to the acrylic body using a 5/64 inches screwdriver to screw the 4x #4-40 screws (4)

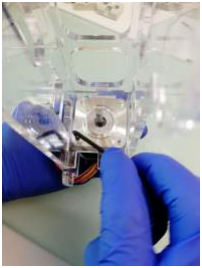
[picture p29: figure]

13. Using 2x M5x25mm hex socket screw (23), the parts (20) and (22) and the ball bearings (21), place them as depicted below

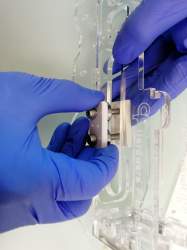
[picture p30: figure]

14. Add the main body and screw the M5 screws into the 3d part
15. Using 2x M5x25mm hex socket screw (23), the parts (25) and (20) and the ball bearings (21), place them as depicted below

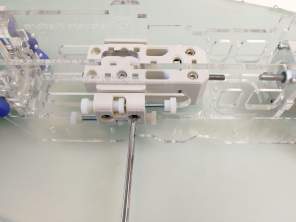
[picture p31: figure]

16. Add the coupler (13) to the motor shaft (3) and M5 rod (9). Important: The shaft and the rod inside the coupler must not be in contact with each other. A thread distance is recommended between them (0.8mm).
a. First screw the coupler into the motor shaft so that the flat part of the shaft is aligned with one of the screws. Attach first that screw not very tight and then attach the second one also not very tight. Then repeat and screw both tightly.
b. On the screws of the rod side, repeat the same process, making sure that the first screw to be screwed is the one that is aligned with whe first one that was screwed on the motor side.

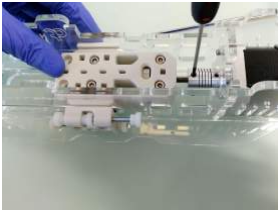
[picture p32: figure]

17. Solder two wires to each limit switch (28) that will connect to the controller board. The forward limit switch wire (in red) should have a length of approximately 37cm whereas the reverse limit switch wires (in black) should have a length of 18 cm.

18. Place the switches as depicted in the picture below, with the front part of the switch aligned with the straight edge of part (29) and with the orange button closer to the top of
(29) when this part is positioned vertically and facing the right side.

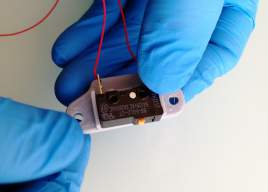
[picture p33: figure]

19. Add the 3D switch cover (27) and screw 2x M2.5 x 12mm Hex Socket Screw (26) to each switch limiter

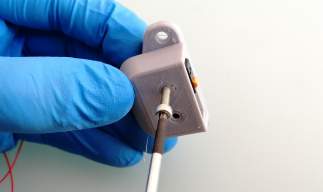
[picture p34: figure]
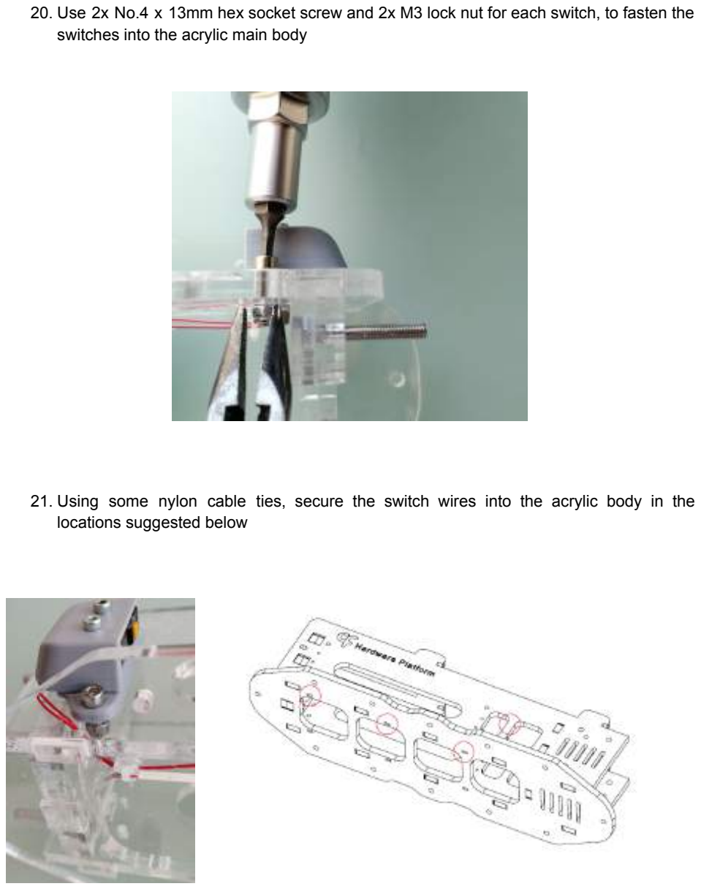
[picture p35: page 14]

20. Use 2x No.4 x 13mm hex socket screw and 2x M3 lock nut for each switch, to fasten the switches into the acrylic main body
21. Using some nylon cable ties, secure the switch wires into the acrylic body in the locations suggested below

22. Attach the 4x M3 nylon screws (36) and 4x M3 nylon (35) to secure the Harp pump board into the acrylic part 2. Place one M3 nylon nut (35) between the acrylic part and the board.

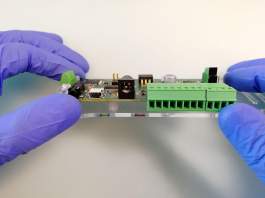
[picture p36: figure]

23. Attach the motor wires to the board in bipolar parallel connection, meaning that the wires will be connected in pairs: red white/yellow -> 1B; red/yellow white -> 1A, orange white/black -> 2A, orange / black white -> 2B.
Screw the switch wires, so that the red wires - forward limit switch - are connected to SW_F connector and black wires - reverse limit switch - are connected to SW_R connector.

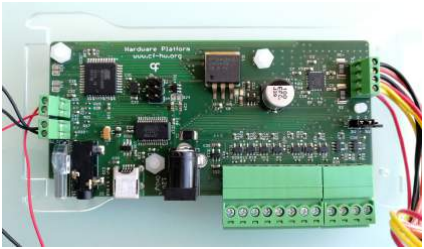
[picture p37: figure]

2

4. A

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
p lid

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
olle

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
ylic

b

o

d

y.

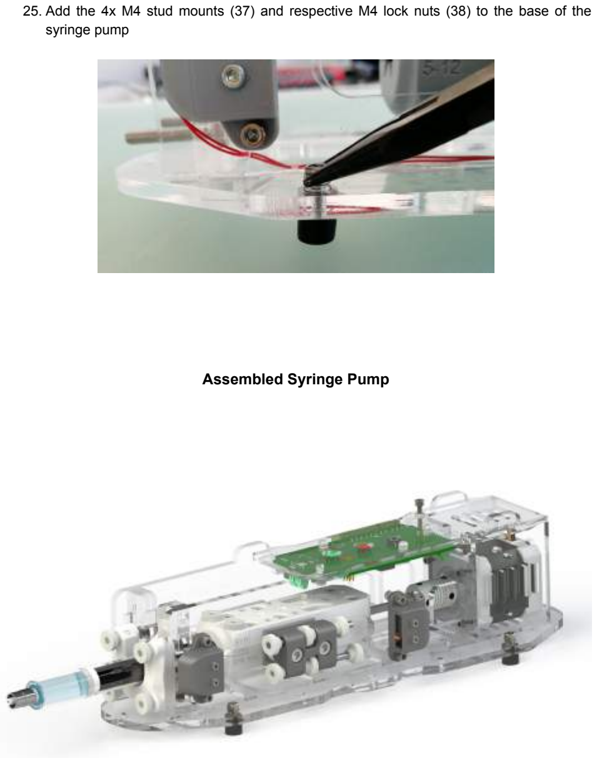
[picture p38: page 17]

25. Add the 4x M4 stud mounts (37) and respective M4 lock nuts (38) to the base of the syringe pump

Assembled Syringe Pump

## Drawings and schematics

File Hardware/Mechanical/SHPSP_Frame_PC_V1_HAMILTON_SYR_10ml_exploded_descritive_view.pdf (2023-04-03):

# Syringe Pump Exploded View SHP

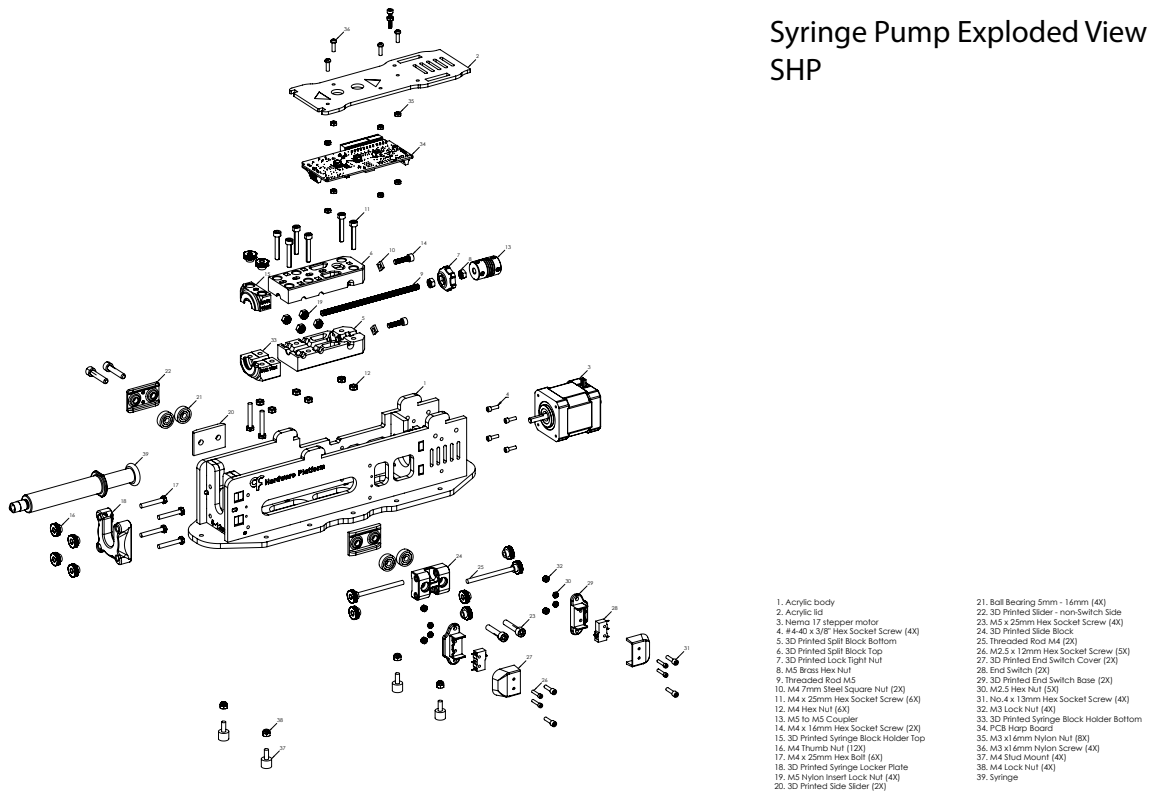
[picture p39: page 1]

1. Acrylic body
2. Acrylic lid
3. Nema 17 stepper motor
4. #4-40 x 3/8" Hex Socket Screw (4X)
5. 3D Printed Split Block Bottom
6. 3D Printed Split Block Top
7. 3D Printed Lock Tight Nut
8. M5 Brass Hex Nut
9. Threaded Rod M5
10. M4 7mm Steel Square Nut (2X)
11. M4 x 25mm Hex Socket Screw (6X)
12. M4 Hex Nut (6X)
13. M5 to M5 Coupler
14. M4 x 16mm Hex Socket Screw (2X)
15. 3D Printed Syringe Block Holder Top
16. M4 Thumb Nut (12X)
17. M4 x 25mm Hex Bolt (6X)
18. 3D Printed Syringe Locker Plate
19. M5 Nylon Insert Lock Nut (4X)
20. 3D Printed Side Slider (2X)

21. Ball Bearing 5mm - 16mm (4X)
22. 3D Printed Slider - non-Switch Side
23. M5 x 25mm Hex Socket Screw (4X)
24. 3D Printed Slide Block
25. Threaded Rod M4 (2X)
26. M2.5 x 12mm Hex Socket Screw (5X)
27. 3D Printed End Switch Cover (2X)
28. End Switch (2X)
29. 3D Printed End Switch Base (2X)
30. M2.5 Hex Nut (5X)
31. No.4 x 13mm Hex Socket Screw (4X)
32. M3 Lock Nut (4X)
33. 3D Printed Syringe Block Holder Bottom
34. PCB Harp Board
35. M3 x16mm Nylon Nut (8X)
36. M3 x16mm Nylon Screw (4X)
37. M4 Stud Mount (4X)
38. M4 Lock Nut (4X)
39. Syringe

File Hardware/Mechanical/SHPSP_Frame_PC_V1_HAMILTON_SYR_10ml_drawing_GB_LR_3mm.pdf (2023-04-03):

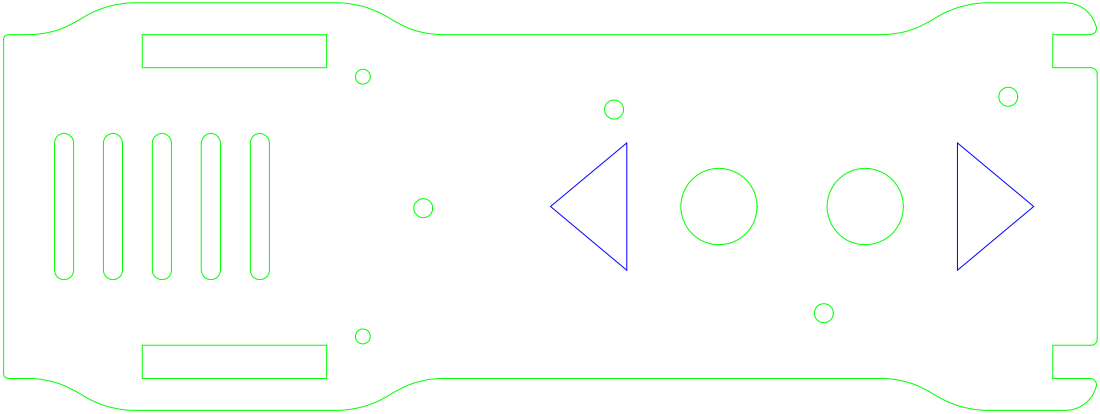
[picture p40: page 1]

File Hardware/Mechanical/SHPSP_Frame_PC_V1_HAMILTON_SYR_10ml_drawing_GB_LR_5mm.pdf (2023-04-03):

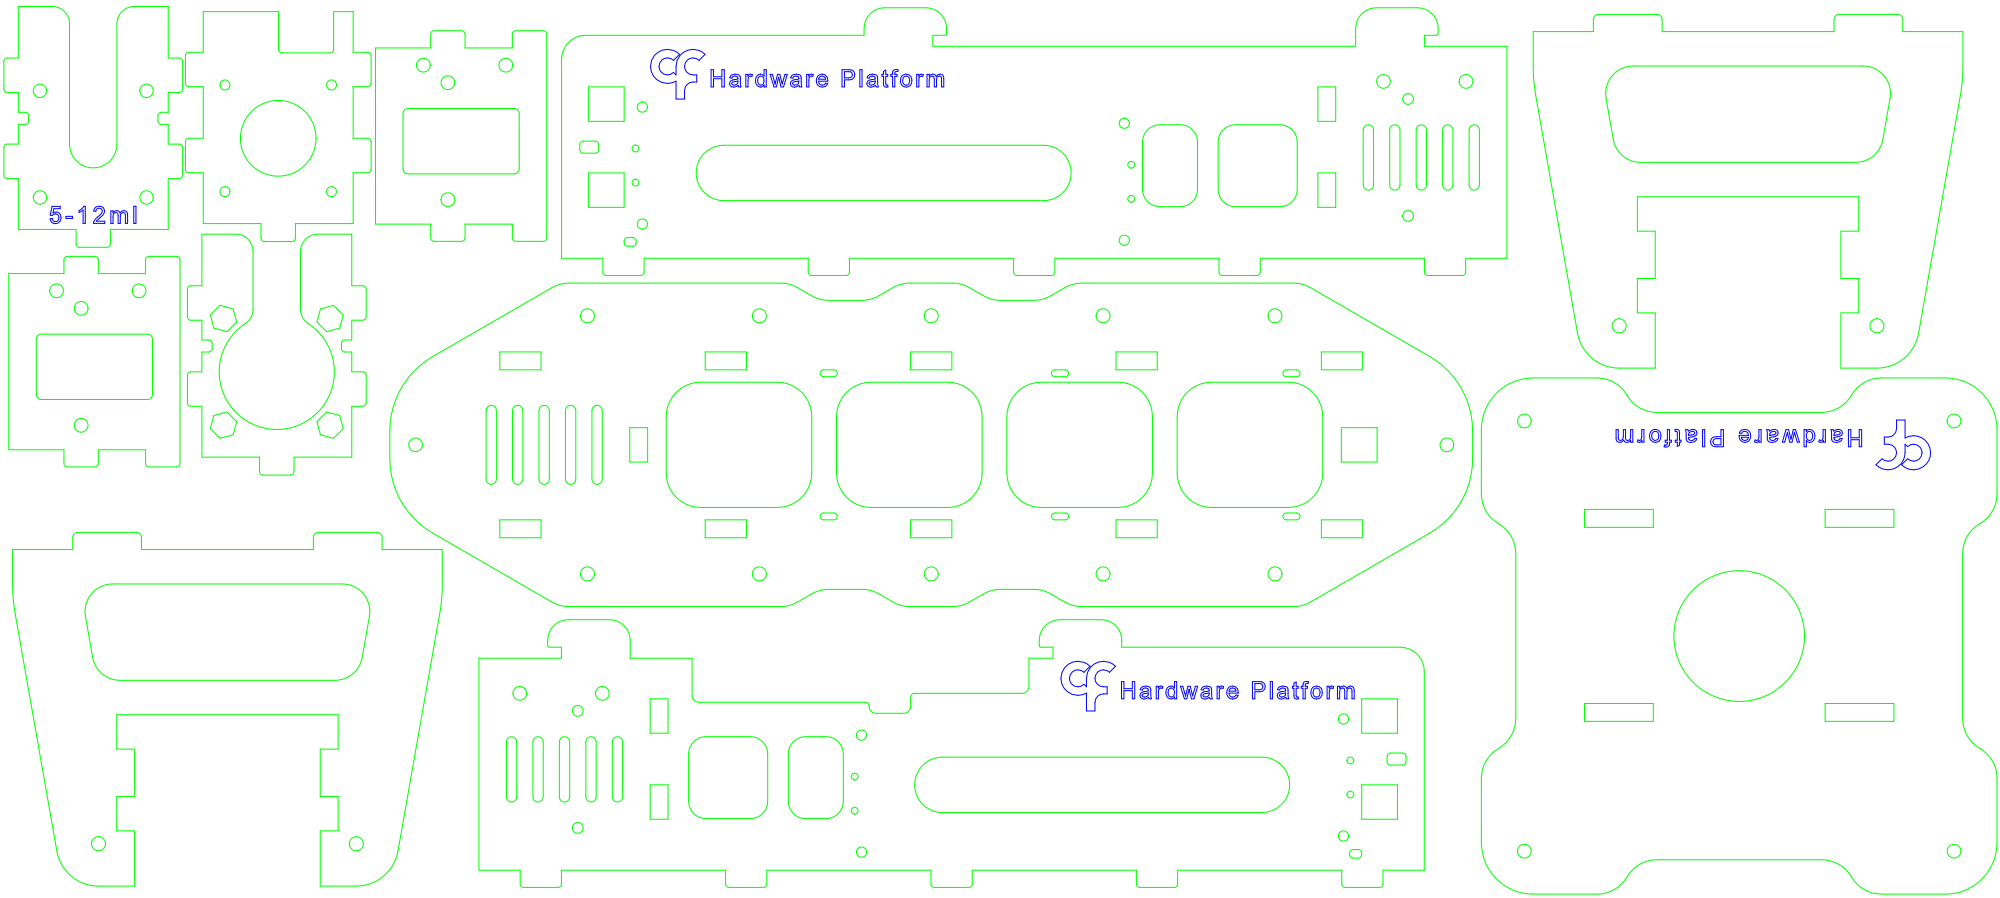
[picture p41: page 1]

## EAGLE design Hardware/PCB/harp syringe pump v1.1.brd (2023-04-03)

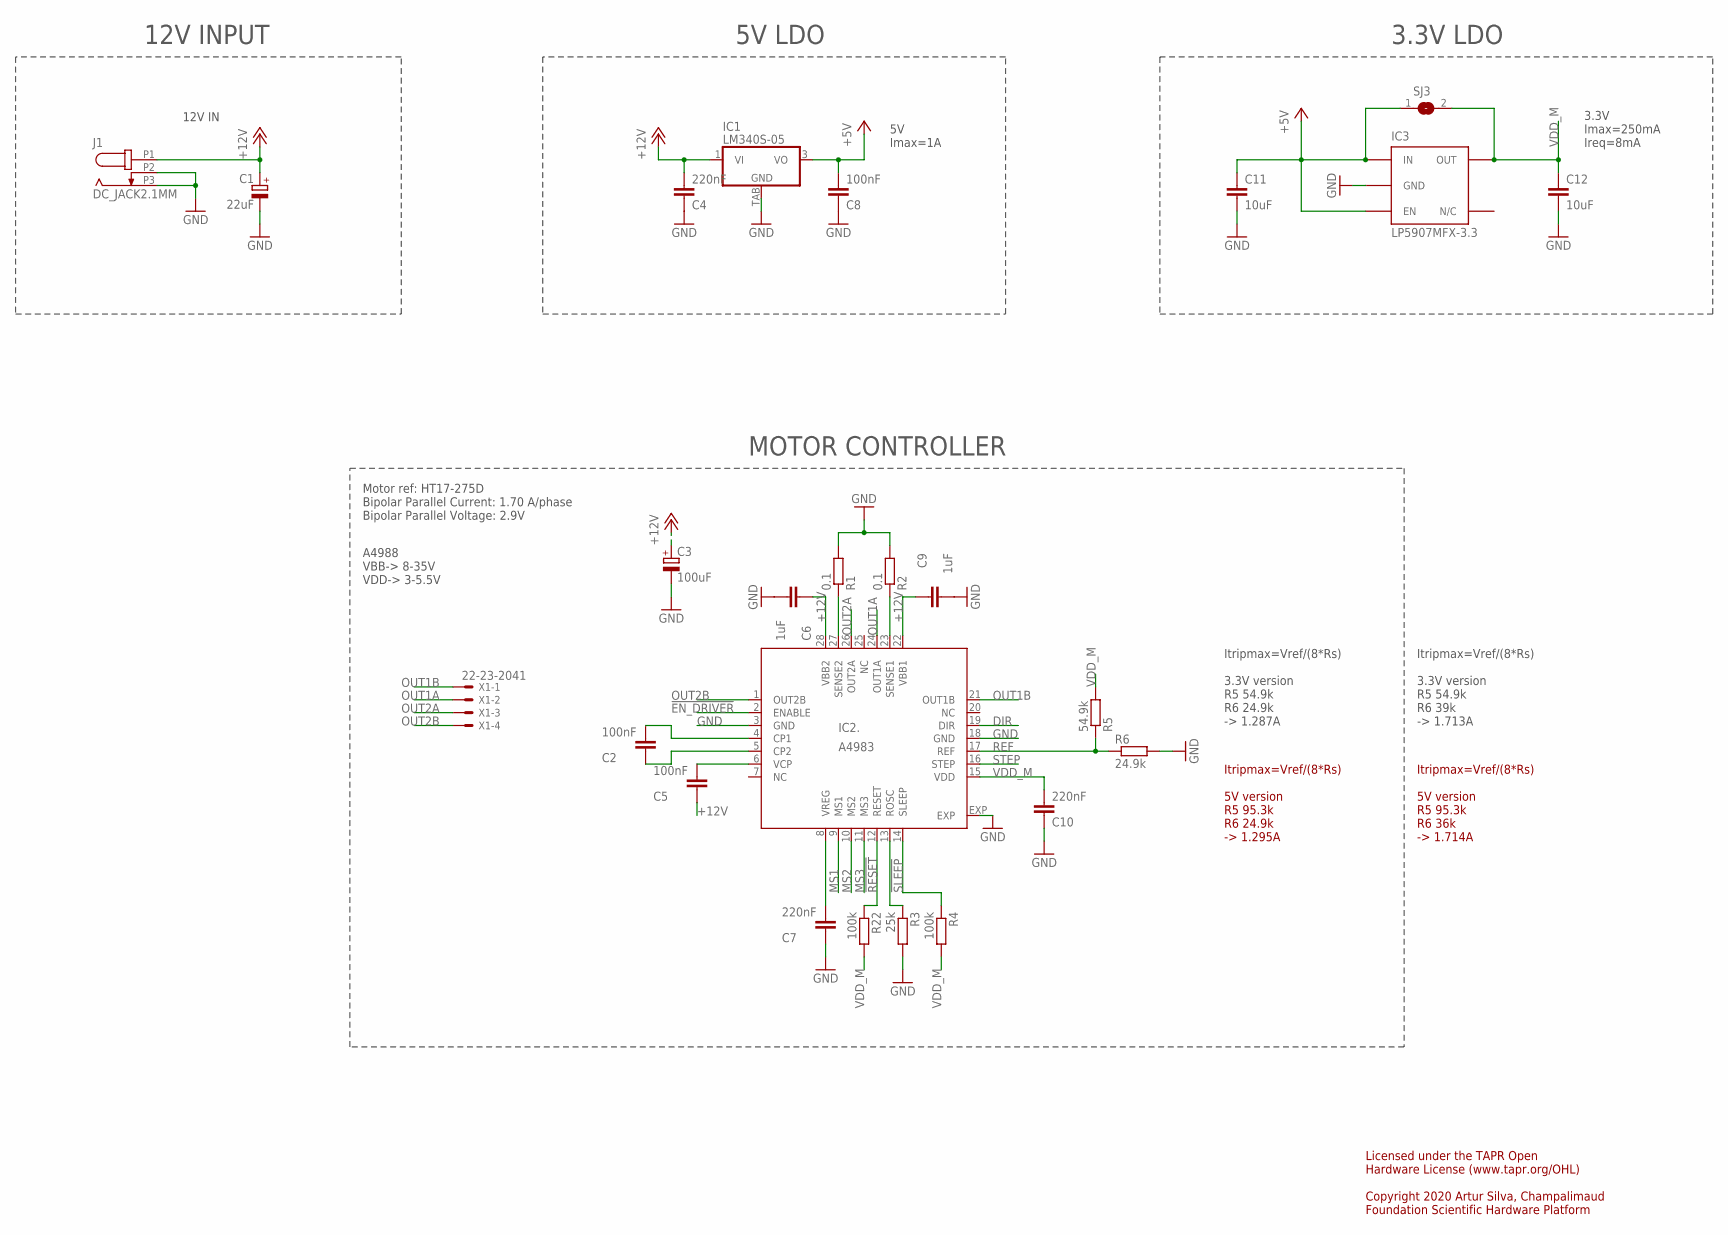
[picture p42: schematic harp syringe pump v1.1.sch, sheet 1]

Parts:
C1: 22uF; CAP_100UF_HAND
C2, C5: 100nF; C0603
C3: 100uF; PANASONIC_E
C4, C7, C10: 220nF; C0603
C6, C9: 1uF; C0603
C8: 100nF; C0402
C11, C12: 10uF; C0603
IC1: LM340S-05; TO263-3
IC2.: A4983; QFN28ET
IC3: LP5907MFX-3.3; TSOT23-5
J1: DC_JACK2.1MM; DC_POWER_INPUT_2.1MM
R1, R2: 0.1; R2010
R3: 25k; R0402
R4, R22: 100k; R0402
R5: 54.9k; R0402
R6: 24.9k; R0402
SJ3: SJ
X1: 22-23-2041

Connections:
!EN_DRIVER: IC2..2 (ENABLE); also elsewhere on the board
!RESET: IC2..12 (RESET), R22.1; also elsewhere on the board
!SLEEP: IC2..14 (SLEEP), R4.1; also elsewhere on the board
+5V: C8.2, C11.1, IC1.3 (VO), IC3.1 (IN), IC3.3 (EN), SJ3.1; also elsewhere on the board
+12V: C1.+, C3.+, C4.2, C5.1, C6.1, C9.1, IC1.1 (VI), IC2..22 (VBB1), IC2..28 (VBB2), J1.P1 (1)
CP1: C2.2, IC2..4 (CP1)
CP2: C2.1, IC2..5 (CP2)
DIR: IC2..19 (DIR); also elsewhere on the board
GND: C1.-, C3.-, C4.1, C6.2, C7.1, C8.1, C9.2, C10.1, C11.2, C12.2, IC1.TAB (GND), IC2..3 (GND), IC2..18 (GND), IC2..EXP, IC3.2 (GND), J1.P2 (2), J1.P3 (3), R1.2, R2.2, R3.2, R6.2; also elsewhere on the board
MS1: IC2..9 (MS1); also elsewhere on the board
MS2: IC2..10 (MS2); also elsewhere on the board
MS3: IC2..11 (MS3); also elsewhere on the board
unnamed: C7.2, IC2..8 (VREG)
unnamed: IC2..13 (ROSC), R3.1
OUT1A: IC2..24 (OUT1A), X1.2
OUT1B: IC2..21 (OUT1B), X1.1
OUT2A: IC2..26 (OUT2A), X1.3
OUT2B: IC2..1 (OUT2B), X1.4
REF: IC2..17 (REF), R5.1, R6.1
SENSE1: IC2..23 (SENSE1), R2.1
SENSE2: IC2..27 (SENSE2), R1.1
STEP: IC2..16 (STEP); also elsewhere on the board
VCP: C5.2, IC2..6 (VCP)
VDD_M: C10.2, C12.1, IC2..15 (VDD), IC3.5 (OUT), R4.2, R5.2, R22.2, SJ3.2

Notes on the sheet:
Licensed under the TAPR Open Hardware License (www.tapr.org/OHL) Copyright 2020 Artur Silva, Champalimaud Foundation Scientific Hardware Platform
12V IN
3.3V Imax=250mA Ireq=8mA
MOTOR CONTROLLER
Motor ref: HT17-275D Bipolar Parallel Current: 1.70 A/phase Bipolar Parallel Voltage: 2.9V
5V LDO
3.3V LDO
12V INPUT
A4988 VBB-> 8-35V VDD-> 3-5.5V
5V Imax=1A
Itripmax=Vref/(8*Rs) 3.3V version R5 54.9k R6 24.9k -> 1.287A
Itripmax=Vref/(8*Rs) 5V version R5 95.3k R6 24.9k -> 1.295A
Itripmax=Vref/(8*Rs) 5V version R5 95.3k R6 36k -> 1.714A
Itripmax=Vref/(8*Rs) 3.3V version R5 54.9k R6 39k -> 1.713A

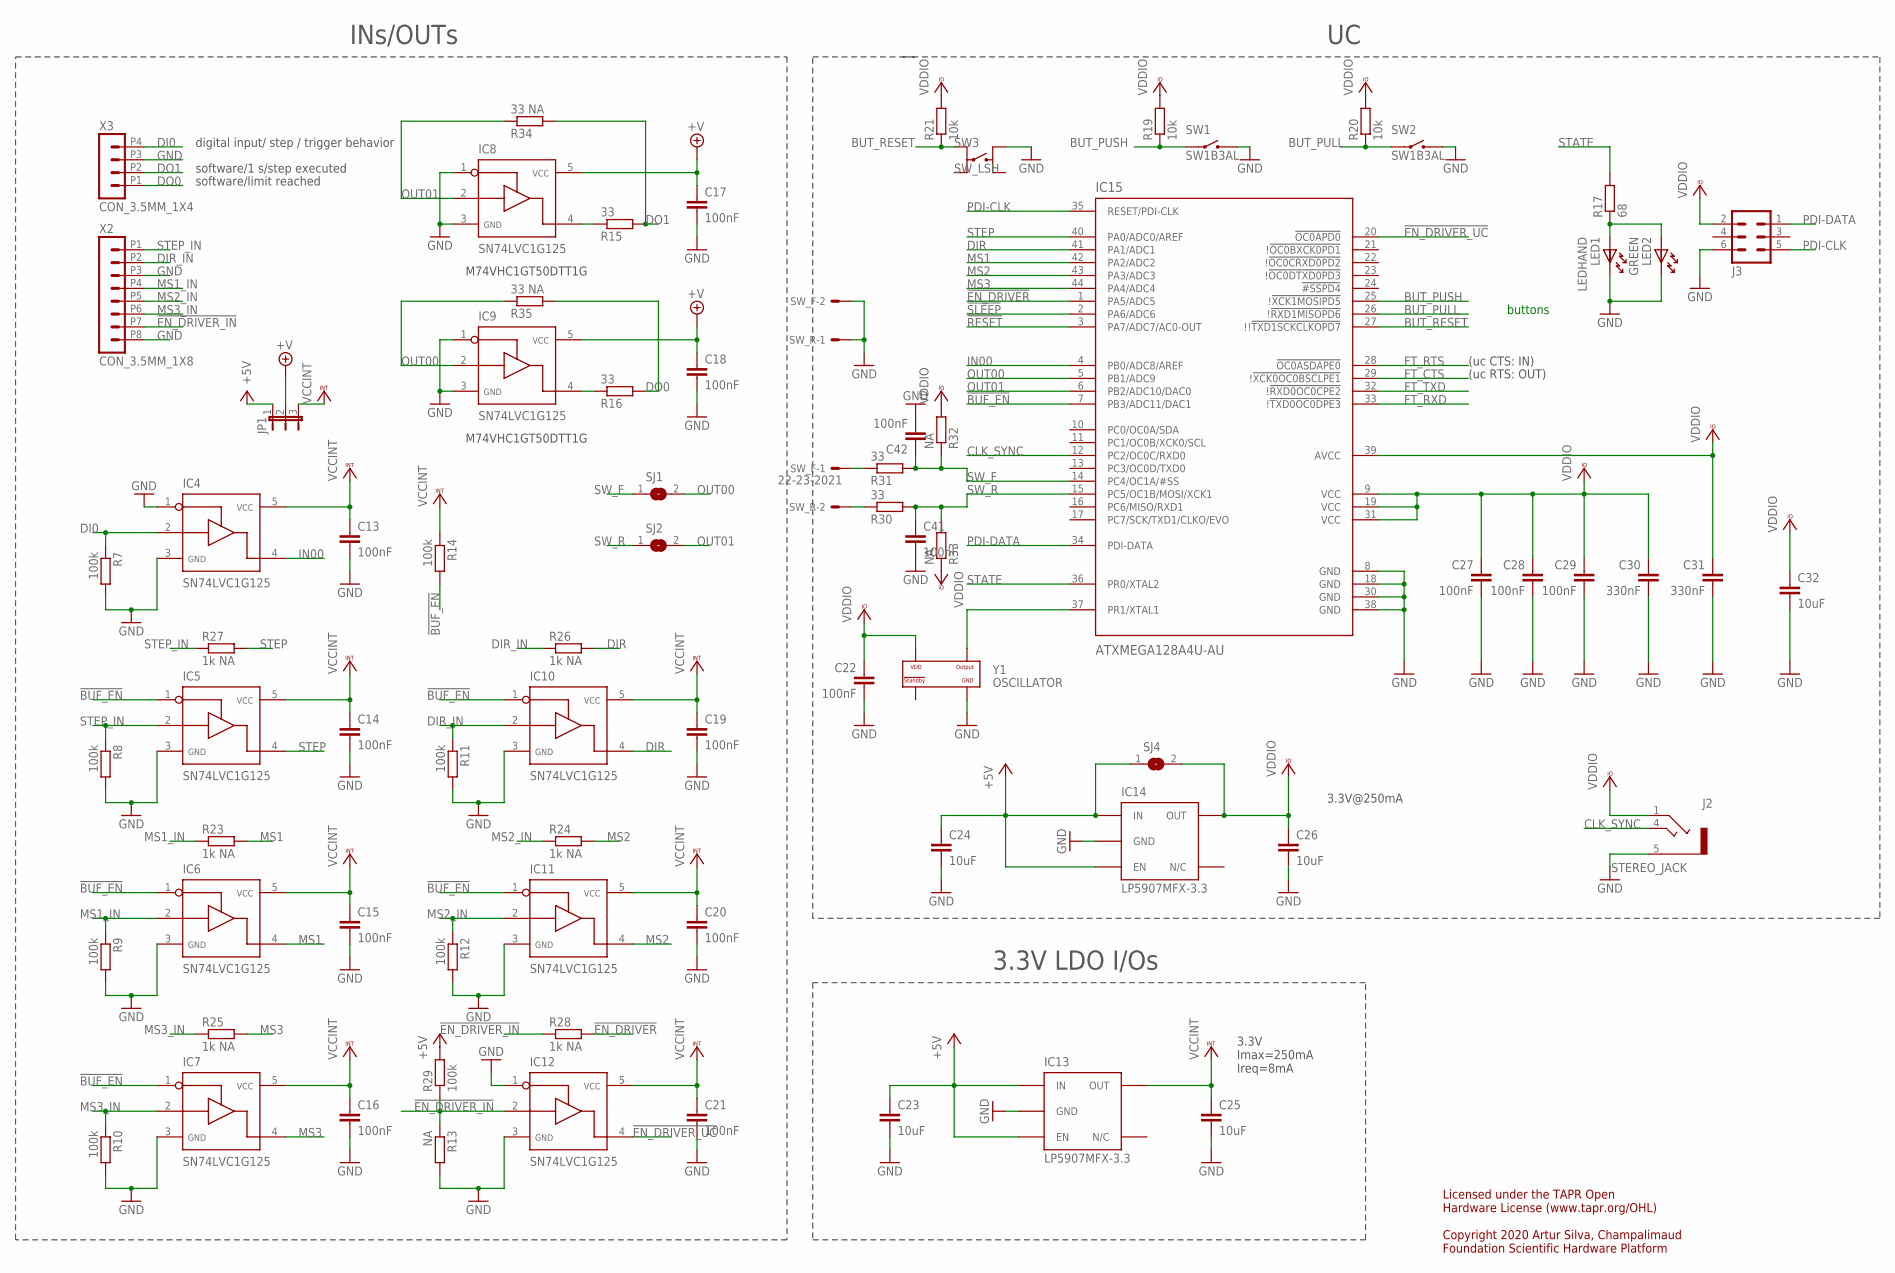
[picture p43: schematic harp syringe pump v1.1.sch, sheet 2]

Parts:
C13, C14, C15, C16, C17, C18, C19, C20, C21, C22, C27, C28, C29, C41, C42: 100nF; C0402
C23, C24, C25, C26, C32: 10uF; C0603
C30, C31: 330nF; C0402
IC4, IC5, IC6, IC7, IC8, IC9, IC10, IC11, IC12: SN74LVC1G125; SOT23-5
IC13, IC14: LP5907MFX-3.3; TSOT23-5
IC15: ATXMEGA128A4U-AU; QFP80P1200X1200X120-44N
J2: STEREO_JACK; 35RASMT2BHNTRX
J3: MA03-2
JP1: JP2E; JP2
LED1: LEDHAND; LED_HAND
LED2: GREEN; LED_HAND
R7, R8, R9, R10, R11, R12, R14, R29: 100k; R0402
R13, R32, R33: NA; R0402
R15, R16, R30, R31: 33; R0402
R17: 68; R0402
R19, R20, R21: 10k; R0402
R23, R24, R25, R26, R27, R28: 1k NA; R0402
R34, R35: 33 NA; R0402
SJ1, SJ2, SJ4: SJ
SW1, SW2: SW1B3AL; SW_B3AL
SW3: SW_LSH; SWITCH_LSH
SW_F: 22-23-2021
SW_R: 22-23-2021
X2: CON_3.5MM_1X8
X3: CON_3.5MM_1X4
Y1: OSCILLATOR; OSCILLATOR_3.2X2.5

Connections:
!BUF_EN: IC5.1, IC6.1, IC7.1, IC10.1, IC11.1, IC15.7 (PB3/ADC11/DAC1), R14.2
!EN_DRIVER: IC15.1 (PA5/ADC5), R28.2; also elsewhere on the board
!EN_DRIVER_IN: IC12.2, R13.1, R28.1, R29.1, X2.P7 (7)
!EN_DRIVER_UC: IC12.4, IC15.20 (!OC0APD0)
!RESET: IC15.3 (PA7/ADC7/AC0-OUT); also elsewhere on the board
!SLEEP: IC15.2 (PA6/ADC6); also elsewhere on the board
+5V: C23.1, C24.1, IC13.1 (IN), IC13.3 (EN), IC14.1 (IN), IC14.3 (EN), JP1.1, R29.2, SJ4.1; also elsewhere on the board
+V: C17.1, C18.1, IC8.5, IC9.5, JP1.2
BUT_PULL: IC15.26 (!!RXD1MISOPD6), R20.1, SW2.P
BUT_PUSH: IC15.25 (!!XCK1MOSIPD5), R19.1, SW1.P
BUT_RESET: IC15.27 (!!!TXD1SCKCLKOPD7), R21.1, SW3.P0
CLK_SYNC: IC15.12 (PC2/OC0C/RXD0), J2.4
DI0: IC4.2, R7.1, X3.P4 (4)
DIR: IC10.4, IC15.41 (PA1/ADC1), R26.2; also elsewhere on the board
DIR_IN: IC10.2, R11.1, R26.1, X2.P2 (2)
DO0: R16.2, R35.2, X3.P1 (1)
DO1: R15.2, R34.2, X3.P2 (2)
FT_CTS: IC15.29 (!!XCK0OC0BSCLPE1); also elsewhere on the board
FT_RTS: IC15.28 (!OC0ASDAPE0); also elsewhere on the board
FT_RXD: IC15.33 (!!TXD0OC0DPE3); also elsewhere on the board
FT_TXD: IC15.32 (!!RXD0OC0CPE2); also elsewhere on the board
GND: C13.2, C14.2, C15.2, C16.2, C17.2, C18.2, C19.2, C20.2, C21.2, C22.2, C23.2, C24.2, C25.2, C26.2, C27.2, C28.2, C29.2, C30.2, C31.2, C32.2, C41.2, C42.2, IC4.1, IC4.3, IC5.3, IC6.3, IC7.3, IC8.1, IC8.3, IC9.1, IC9.3, IC10.3, IC11.3, IC12.1, IC12.3, IC13.2 (GND), IC14.2 (GND), IC15.8 (GND), IC15.18 (GND), IC15.30 (GND), IC15.38 (GND), J2.5, J3.6, LED1.K, LED2.K, R7.2, R8.2, R9.2, R10.2, R11.2, R12.2, R13.2, SW1.O, SW2.O, SW3.O0 (O), SW_F.2, SW_R.1, X2.P3 (3), X2.P8 (8), X3.P3 (3), Y1.P$2 (GND); also elsewhere on the board
IN00: IC4.4, IC15.4 (PB0/ADC8/AREF)
MS1: IC6.4, IC15.42 (PA2/ADC2), R23.2; also elsewhere on the board
MS1_IN: IC6.2, R9.1, R23.1, X2.P4 (4)
MS2: IC11.4, IC15.43 (PA3/ADC3), R24.2; also elsewhere on the board
MS2_IN: IC11.2, R12.1, R24.1, X2.P5 (5)
MS3: IC7.4, IC15.44 (PA4/ADC4), R25.2; also elsewhere on the board
MS3_IN: IC7.2, R10.1, R25.1, X2.P6 (6)
unnamed: IC8.4, R15.1
unnamed: R30.1, SW_R.2
unnamed: R31.1, SW_F.1
unnamed: IC9.4, R16.1
unnamed: LED1.A, LED2.A, R17.1
OSC1: IC15.37 (PR1/XTAL1), Y1.P$3 (OUTPUT)
OUT00: IC9.2, IC15.5 (PB1/ADC9), R35.1, SJ1.2
OUT01: IC8.2, IC15.6 (PB2/ADC10/DAC0), R34.1, SJ2.2
PDI-CLK: IC15.35 (RESET/PDI-CLK), J3.5
PDI-DATA: IC15.34 (PDI-DATA), J3.1
STATE: IC15.36 (PR0/XTAL2), R17.2
STEP: IC5.4, IC15.40 (PA0/ADC0/AREF), R27.2; also elsewhere on the board
STEP_IN: IC5.2, R8.1, R27.1, X2.P1 (1)
SW_F: C42.1, IC15.14 (PC4/OC1A/#SS), R31.2, R32.1, SJ1.1
SW_R: C41.1, IC15.15 (PC5/OC1B/MOSI/XCK1), R30.2, R33.2, SJ2.1
VCCINT: C13.1, C14.1, C15.1, C16.1, C19.1, C20.1, C21.1, C25.1, IC4.5, IC5.5, IC6.5, IC7.5, IC10.5, IC11.5, IC12.5, IC13.5 (OUT), JP1.3, R14.1
VCCIO: C22.1, C26.1, C27.1, C28.1, C29.1, C30.1, C31.1, C32.1, IC14.5 (OUT), IC15.9 (VCC), IC15.19 (VCC), IC15.31 (VCC), IC15.39 (AVCC), J2.1, J3.2, R19.2, R20.2, R21.2, R32.2, R33.1, SJ4.2, Y1.P$4 (VDD)

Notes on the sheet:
3.3V@250mA
(uc CTS: IN)
(uc RTS: OUT)
buttons
M74VHC1GT50DTT1G
INs/OUTs
digital input/ step / trigger behavior
software/1 s/step executed
software/limit reached
3.3V Imax=250mA Ireq=8mA
3.3V LDO I/Os
Licensed under the TAPR Open Hardware License (www.tapr.org/OHL) Copyright 2020 Artur Silva, Champalimaud Foundation Scientific Hardware Platform

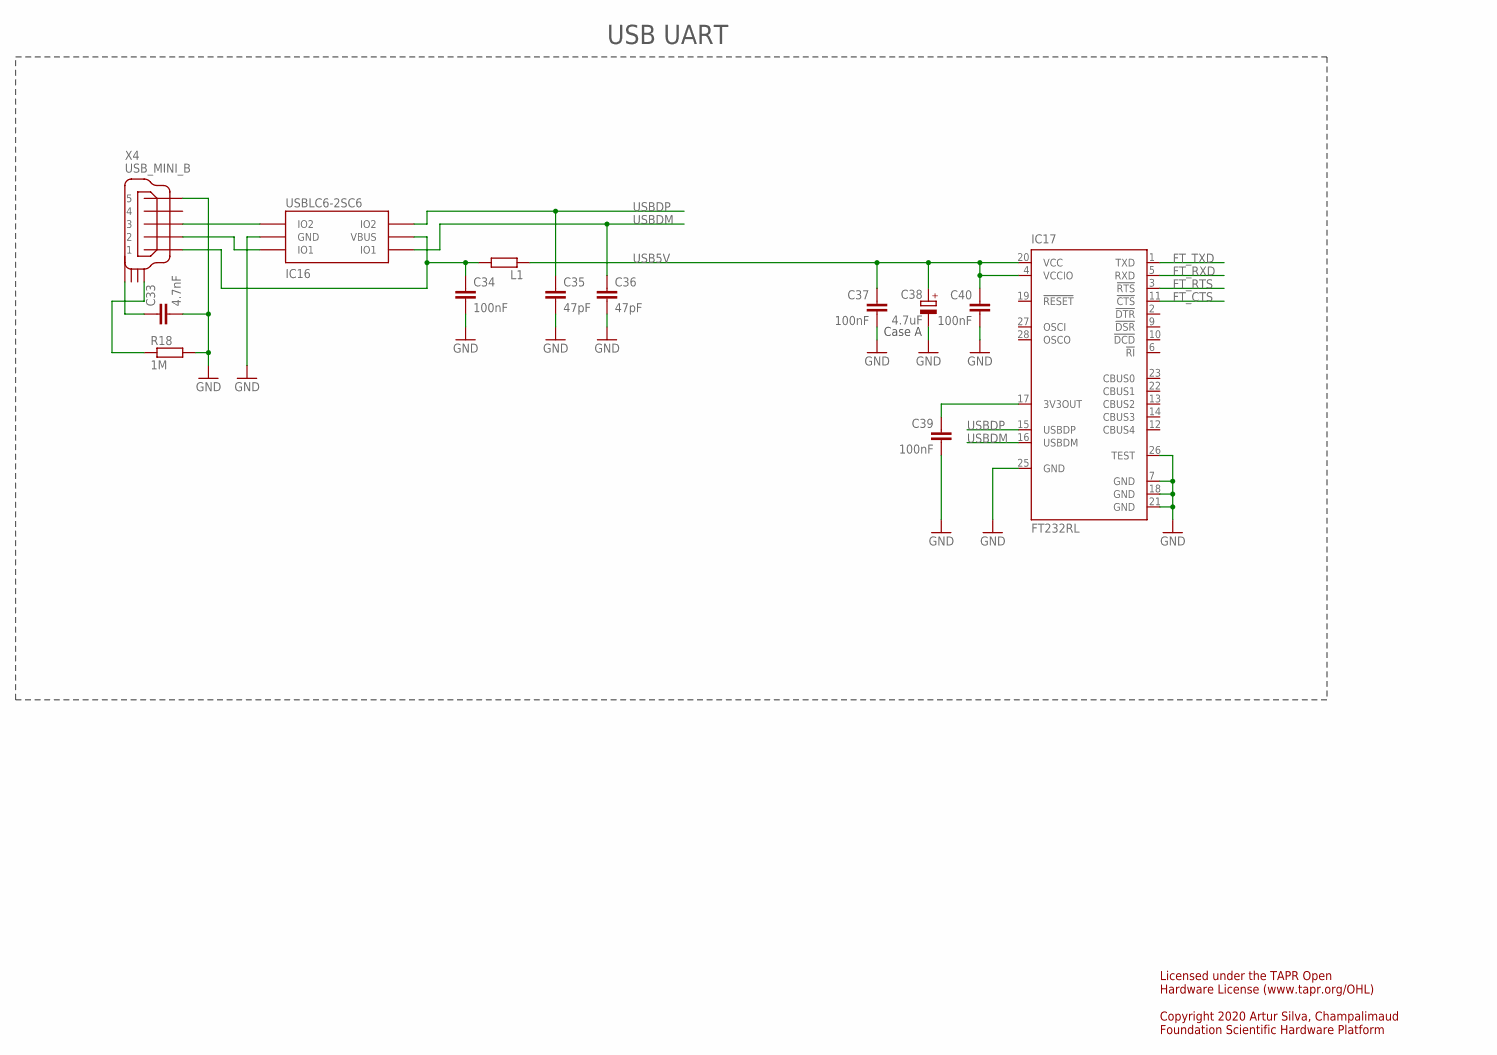
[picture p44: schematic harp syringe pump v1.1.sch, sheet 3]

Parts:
C33: 4.7nF; C0402
C34, C37, C39, C40: 100nF; C0402
C35, C36: 47pF; C0402
C38: 4.7uF; A/3216-18W
IC16: USBLC6-2SC6; SOT23-6L
IC17: FT232RL; SSOP28
L1: ???; R0805
R18: 1M; R0402
X4: USB_MINI_B; 240-0002-1

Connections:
3V3OUT: C39.1, IC17.17 (3V3OUT)
FT_CTS: IC17.11 (!CTS); also elsewhere on the board
FT_RTS: IC17.3 (!RTS); also elsewhere on the board
FT_RXD: IC17.5 (RXD); also elsewhere on the board
FT_TXD: IC17.1 (TXD); also elsewhere on the board
GND: C33.2, C34.2, C35.2, C36.2, C37.2, C38.-, C39.2, C40.2, IC16.P$2 (GND), IC17.7 (GND), IC17.18 (GND), IC17.21 (GND), IC17.25 (GND), IC17.26 (TEST), R18.2, X4.P$5 (5); also elsewhere on the board
unnamed: IC16.P$3 (IO2), X4.P$3 (3)
unnamed: C33.1, X4.SHIELD_4
unnamed: C34.1, IC16.P$5 (VBUS), L1.2, X4.P$1 (1)
unnamed: R18.1, X4.SHIELD_1
unnamed: IC16.P$1 (IO1), X4.P$2 (2)
USB5V: C37.1, C38.+, C40.1, IC17.4 (VCCIO), IC17.20 (VCC), L1.1
USBDM: C36.1, IC16.P$6 (IO1), IC17.16 (USBDM)
USBDP: C35.1, IC16.P$4 (IO2), IC17.15 (USBDP)

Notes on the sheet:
Case A
USB UART
Licensed under the TAPR Open Hardware License (www.tapr.org/OHL) Copyright 2020 Artur Silva, Champalimaud Foundation Scientific Hardware Platform

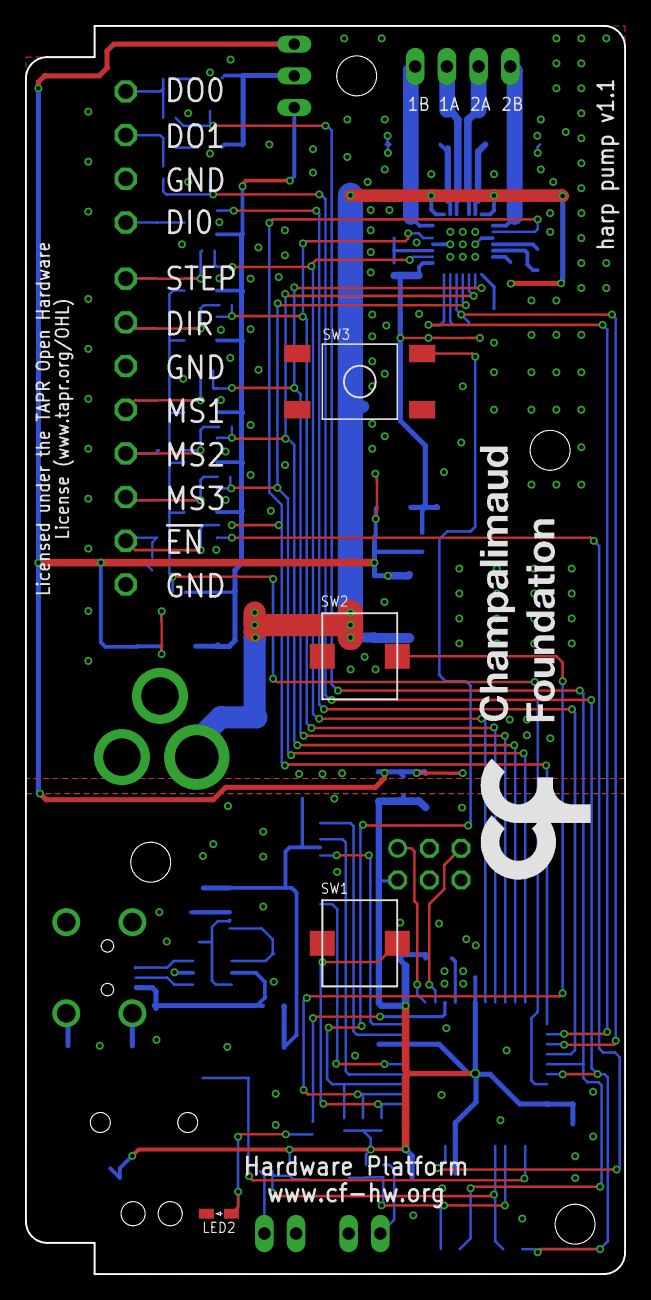
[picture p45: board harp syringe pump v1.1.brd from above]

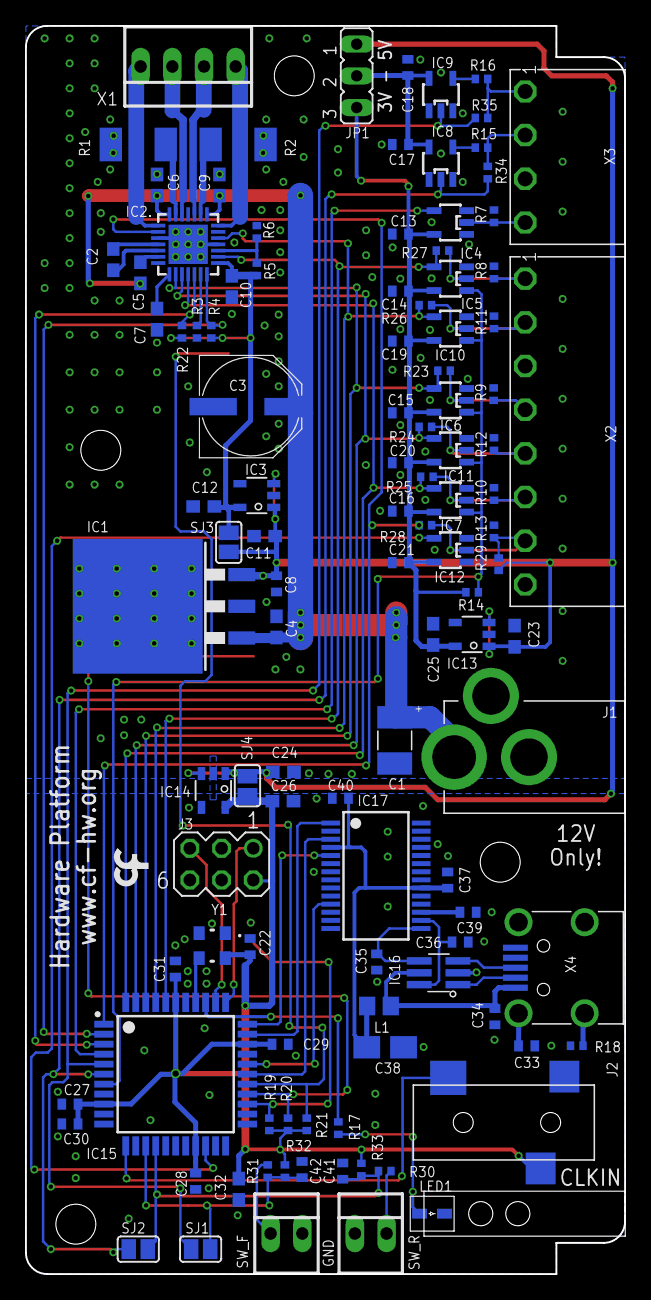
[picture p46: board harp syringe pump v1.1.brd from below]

Board: 2 copper layers, 48.0 x 100.0 mm, 118 parts (113 on the bottom side), 69 nets.

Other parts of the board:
U$2: LOGO_5
U$3: LED_PIPE_7513D2-L
U$4: LOGO_8

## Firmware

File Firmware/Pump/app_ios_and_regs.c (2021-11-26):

#include <avr/io.h>
#include "hwbp_core_types.h"
#include "app_ios_and_regs.h"

/************************************************************************/
/* Configure and initialize IOs                                         */
/************************************************************************/
void init_ios(void)
{	/* Configure input pins */
	io_pin2in(&PORTB, 0, PULL_IO_TRISTATE, SENSE_IO_EDGES_BOTH);         // IN00
	io_pin2in(&PORTC, 0, PULL_IO_DOWN, SENSE_IO_EDGES_BOTH);             // TYPE0
	io_pin2in(&PORTC, 1, PULL_IO_DOWN, SENSE_IO_EDGES_BOTH);             // TYPE1
	io_pin2in(&PORTC, 4, PULL_IO_UP, SENSE_IO_EDGES_BOTH);               // SW_F
	io_pin2in(&PORTC, 5, PULL_IO_UP, SENSE_IO_EDGES_BOTH);               // SW_R
	io_pin2in(&PORTD, 0, PULL_IO_TRISTATE, SENSE_IO_EDGES_BOTH);         // EN_DRIVER_UC
	io_pin2in(&PORTD, 5, PULL_IO_UP, SENSE_IO_EDGES_BOTH);               // BUT_PUSH
	io_pin2in(&PORTD, 6, PULL_IO_UP, SENSE_IO_EDGES_BOTH);               // BUT_PULL
	io_pin2in(&PORTD, 7, PULL_IO_UP, SENSE_IO_EDGES_BOTH);               // BUT_RESET

	/* Configure input interrupts */
	io_set_int(&PORTB, INT_LEVEL_LOW, 0, (1<<0), false);                 // IN00
	io_set_int(&PORTC, INT_LEVEL_LOW, 0, (1<<0), false);                 // TYPE0
	io_set_int(&PORTC, INT_LEVEL_LOW, 0, (1<<1), false);                 // TYPE1
	io_set_int(&PORTC, INT_LEVEL_LOW, 0, (1<<4), false);                 // SW_F
	io_set_int(&PORTC, INT_LEVEL_LOW, 0, (1<<5), false);                 // SW_R
	io_set_int(&PORTD, INT_LEVEL_LOW, 0, (1<<0), false);                 // EN_DRIVER_UC
	io_set_int(&PORTD, INT_LEVEL_LOW, 0, (1<<5), false);                 // BUT_PUSH
	io_set_int(&PORTD, INT_LEVEL_LOW, 0, (1<<6), false);                 // BUT_PULL
	io_set_int(&PORTD, INT_LEVEL_LOW, 0, (1<<7), false);                 // BUT_RESET

	/* Configure output pins */
	io_pin2out(&PORTA, 0, OUT_IO_DIGITAL, IN_EN_IO_EN);                  // STEP
	io_pin2out(&PORTA, 1, OUT_IO_DIGITAL, IN_EN_IO_EN);                  // DIR
	io_pin2out(&PORTA, 2, OUT_IO_DIGITAL, IN_EN_IO_DIS);                 // MS1
	io_pin2out(&PORTA, 3, OUT_IO_DIGITAL, IN_EN_IO_DIS);                 // MS2
	io_pin2out(&PORTA, 4, OUT_IO_DIGITAL, IN_EN_IO_DIS);                 // MS3
	io_pin2out(&PORTA, 5, OUT_IO_DIGITAL, IN_EN_IO_EN);                  // EN_DRIVER
	io_pin2out(&PORTA, 6, OUT_IO_DIGITAL, IN_EN_IO_DIS);                 // SLEEP
	io_pin2out(&PORTA, 7, OUT_IO_DIGITAL, IN_EN_IO_DIS);                 // RESET
	io_pin2out(&PORTB, 1, OUT_IO_DIGITAL, IN_EN_IO_EN);                  // OUT00
	io_pin2out(&PORTB, 2, OUT_IO_DIGITAL, IN_EN_IO_EN);                  // OUT01
	io_pin2out(&PORTB, 3, OUT_IO_DIGITAL, IN_EN_IO_DIS);                 // BUF_EN

	/* Initialize output pins */
	clr_STEP;
	clr_DIR;
	clr_MS1;
	clr_MS2;
	clr_MS3;
	set_EN_DRIVER;
	set_SLEEP;
	set_RESET;
	clr_OUT00;
	clr_OUT01;
	set_BUF_EN;
}

/************************************************************************/
/* Registers' stuff                                                     */
/************************************************************************/
AppRegs app_regs;

uint8_t app_regs_type[] = {
	TYPE_U8,
	TYPE_U8,
	TYPE_U8,
	TYPE_U8,
	TYPE_U8,
	TYPE_U8,
	TYPE_U8,
	TYPE_U8,
	TYPE_U8,
	TYPE_U8,
	TYPE_U8,
	TYPE_U8,
	TYPE_U8,
	TYPE_U16,
	TYPE_FLOAT,
	TYPE_U16,
	TYPE_FLOAT,
	TYPE_U8,
	TYPE_U8,
	TYPE_U8,
	TYPE_U8,
	TYPE_U8,
	TYPE_U8,
	TYPE_U8
};

uint16_t app_regs_n_elements[] = {
	1,
	1,
	1,
	1,
	1,
	1,
	1,
	1,
	1,
	1,
	1,
	1,
	1,
	1,
	1,
	1,
	1,
	1,
	1,
	1,
	1,
	1,
	1,
	1
};

uint8_t *app_regs_pointer[] = {
	(uint8_t*)(&app_regs.REG_ENABLE_MOTOR_DRIVER),
	(uint8_t*)(&app_regs.REG_START_PROTOCOL),
	(uint8_t*)(&app_regs.REG_STEP_STATE),
	(uint8_t*)(&app_regs.REG_DIR_STATE),
	(uint8_t*)(&app_regs.REG_SW_FORWARD_STATE),
	(uint8_t*)(&app_regs.REG_SW_REVERSE_STATE),
	(uint8_t*)(&app_regs.REG_INPUT_STATE),
	(uint8_t*)(&app_regs.REG_SET_DOS),
	(uint8_t*)(&app_regs.REG_CLEAR_DOS),
	(uint8_t*)(&app_regs.REG_DO0_CONFIG),
	(uint8_t*)(&app_regs.REG_DO1_CONFIG),
	(uint8_t*)(&app_regs.REG_DI0_CONFIG),
	(uint8_t*)(&app_regs.REG_MOTOR_MICROSTEP),
	(uint8_t*)(&app_regs.REG_PROTOCOL_NUMBER_STEPS),
	(uint8_t*)(&app_regs.REG_PROTOCOL_FLOWRATE),
	(uint8_t*)(&app_regs.REG_PROTOCOL_PERIOD),
	(uint8_t*)(&app_regs.REG_PROTOCOL_VOLUME),
	(uint8_t*)(&app_regs.REG_PROTOCOL_TYPE),
	(uint8_t*)(&app_regs.REG_CALIBRATION_VALUE_1),
	(uint8_t*)(&app_regs.REG_CALIBRATION_VALUE_2),
	(uint8_t*)(&app_regs.REG_EVT_ENABLE),
	(uint8_t*)(&app_regs.REG_SET_BOARD_TYPE),
	(uint8_t*)(&app_regs.REG_PROTOCOL_STATE),
	(uint8_t*)(&app_regs.REG_PROTOCOL_DIRECTION)
};

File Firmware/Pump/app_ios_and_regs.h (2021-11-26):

#ifndef _APP_IOS_AND_REGS_H_
#define _APP_IOS_AND_REGS_H_
#include "cpu.h"

void init_ios(void);
/************************************************************************/
/* Definition of input pins                                             */
/************************************************************************/
// IN00                   Description: Board digital input 0
// TYPE0                  Description: Board type pin 0
// TYPE1                  Description: Board type pin 1. If pin 0 == 1 -> FISH_FEEDER. If both are 0 == pump. If pin 1 == 1 STEP_MOTOR
// SW_F                   Description: Limit switch signal (forward)
// SW_R                   Description: Limit switch signal (reverse)
// EN_DRIVER_UC           Description: Enable driver from user output
// BUT_PUSH               Description: Button to push syringe
// BUT_PULL               Description: Button to pull syringe
// BUT_RESET              Description: Button to reset to initial state

#define read_IN00 read_io(PORTB, 0)             // IN00
#define read_TYPE0 read_io(PORTC, 0)            // TYPE0
#define read_TYPE1 read_io(PORTC, 1)            // TYPE1
#define read_SW_F read_io(PORTC, 4)             // SW_F
#define read_SW_R read_io(PORTC, 5)             // SW_R
#define read_EN_DRIVER_UC read_io(PORTD, 0)     // EN_DRIVER_UC
#define read_BUT_PUSH read_io(PORTD, 5)         // BUT_PUSH
#define read_BUT_PULL read_io(PORTD, 6)         // BUT_PULL
#define read_BUT_RESET read_io(PORTD, 7)        // BUT_RESET

/************************************************************************/
/* Definition of output pins                                            */
/************************************************************************/
// STEP                   Description: Motor controller input step
// DIR                    Description: Motor controller direction input
// MS1                    Description: Motor configuration bit 1
// MS2                    Description: Motor configuration bit 2
// MS3                    Description: Motor configuration bit 3
// EN_DRIVER              Description: Motor controller enable
// SLEEP                  Description: Motor controller sleep
// RESET                  Description: Motor controller reset
// OUT00                  Description: Board digital output 0
// OUT01                  Description: Board digital output 1
// BUF_EN                 Description: Enable signal for user controller inputs

/* STEP */
#define set_STEP set_io(PORTA, 0)
#define clr_STEP clear_io(PORTA, 0)
#define tgl_STEP toggle_io(PORTA, 0)
#define read_STEP read_io(PORTA, 0)

/* DIR */
#define set_DIR set_io(PORTA, 1)
#define clr_DIR clear_io(PORTA, 1)
#define tgl_DIR toggle_io(PORTA, 1)
#define read_DIR read_io(PORTA, 1)

/* MS1 */
#define set_MS1 set_io(PORTA, 2)
#define clr_MS1 clear_io(PORTA, 2)
#define tgl_MS1 toggle_io(PORTA, 2)
#define read_MS1 read_io(PORTA, 2)

/* MS2 */
#define set_MS2 set_io(PORTA, 3)
#define clr_MS2 clear_io(PORTA, 3)
#define tgl_MS2 toggle_io(PORTA, 3)
#define read_MS2 read_io(PORTA, 3)

/* MS3 */
#define set_MS3 set_io(PORTA, 4)
#define clr_MS3 clear_io(PORTA, 4)
#define tgl_MS3 toggle_io(PORTA, 4)
#define read_MS3 read_io(PORTA, 4)

/* EN_DRIVER */
#define set_EN_DRIVER clear_io(PORTA, 5)
#define clr_EN_DRIVER set_io(PORTA, 5)
#define tgl_EN_DRIVER toggle_io(PORTA, 5)
#define read_EN_DRIVER read_io(PORTA, 5)

/* SLEEP */
#define set_SLEEP clear_io(PORTA, 6)
#define clr_SLEEP set_io(PORTA, 6)
#define tgl_SLEEP toggle_io(PORTA, 6)
#define read_SLEEP read_io(PORTA, 6)

/* RESET */
#define set_RESET clear_io(PORTA, 7)
#define clr_RESET set_io(PORTA, 7)
#define tgl_RESET toggle_io(PORTA, 7)
#define read_RESET read_io(PORTA, 7)

/* OUT00 */
#define set_OUT00 set_io(PORTB, 1)
#define clr_OUT00 clear_io(PORTB, 1)
#define tgl_OUT00 toggle_io(PORTB, 1)
#define read_OUT00 read_io(PORTB, 1)

/* OUT01 */
#define set_OUT01 set_io(PORTB, 2)
#define clr_OUT01 clear_io(PORTB, 2)
#define tgl_OUT01 toggle_io(PORTB, 2)
#define read_OUT01 read_io(PORTB, 2)

/* BUF_EN */
#define set_BUF_EN clear_io(PORTB, 3)
#define clr_BUF_EN set_io(PORTB, 3)
#define tgl_BUF_EN toggle_io(PORTB, 3)
#define read_BUF_EN read_io(PORTB, 3)


/************************************************************************/
/* Registers' structure                                                 */
/************************************************************************/
typedef struct
{
	uint8_t REG_ENABLE_MOTOR_DRIVER;
	uint8_t REG_START_PROTOCOL;
	uint8_t REG_STEP_STATE;
	uint8_t REG_DIR_STATE;
	uint8_t REG_SW_FORWARD_STATE;
	uint8_t REG_SW_REVERSE_STATE;
	uint8_t REG_INPUT_STATE;
	uint8_t REG_SET_DOS;
	uint8_t REG_CLEAR_DOS;
	uint8_t REG_DO0_CONFIG;
	uint8_t REG_DO1_CONFIG;
	uint8_t REG_DI0_CONFIG;
	uint8_t REG_MOTOR_MICROSTEP;
	uint16_t REG_PROTOCOL_NUMBER_STEPS;
	float REG_PROTOCOL_FLOWRATE;
	uint16_t REG_PROTOCOL_PERIOD;
	float REG_PROTOCOL_VOLUME;
	uint8_t REG_PROTOCOL_TYPE;
	uint8_t REG_CALIBRATION_VALUE_1;
	uint8_t REG_CALIBRATION_VALUE_2;
	uint8_t REG_EVT_ENABLE;
	uint8_t REG_SET_BOARD_TYPE;
	uint8_t REG_PROTOCOL_STATE;
	uint8_t REG_PROTOCOL_DIRECTION;
} AppRegs;

/************************************************************************/
/* Registers' address                                                   */
/************************************************************************/
/* Registers */
#define ADD_REG_ENABLE_MOTOR_DRIVER         32 // U8     Enable the motor driver
#define ADD_REG_START_PROTOCOL              33 // U8     Enable the defined protocol
#define ADD_REG_STEP_STATE                  34 // U8     Control the step of the motor controller
#define ADD_REG_DIR_STATE                   35 // U8     Control the direction of the motor controller
#define ADD_REG_SW_FORWARD_STATE            36 // U8     State of the forward switch limit
#define ADD_REG_SW_REVERSE_STATE            37 // U8     State of the reverse switch limit
#define ADD_REG_INPUT_STATE                 38 // U8     Value of input 0 pin
#define ADD_REG_SET_DOS                     39 // U8     Set digital outputs
#define ADD_REG_CLEAR_DOS                   40 // U8     Clear digital outputs
#define ADD_REG_DO0_CONFIG                  41 // U8     Configures which signal is connected to the digital output 0
#define ADD_REG_DO1_CONFIG                  42 // U8     Configures which signal is connected to the digital output 1
#define ADD_REG_DI0_CONFIG                  43 // U8     Configuration of the digital input 0 (DI0)
#define ADD_REG_MOTOR_MICROSTEP             44 // U8     Defines the motor microstep
#define ADD_REG_PROTOCOL_NUMBER_STEPS       45 // U16    Number of steps [1;65535]
#define ADD_REG_PROTOCOL_FLOWRATE           46 // FLOAT  Flowrate value in uL/s ]0;max_float[
#define ADD_REG_PROTOCOL_PERIOD             47 // U16    Period for each step in ms [1;65535]
#define ADD_REG_PROTOCOL_VOLUME             48 // FLOAT  Volume value in uL ]0;max_float[
#define ADD_REG_PROTOCOL_TYPE               49 // U8     Step-based (0) or Volume-based protocol (1)
#define ADD_REG_CALIBRATION_VALUE_1         50 // U8     Calibration value 1
#define ADD_REG_CALIBRATION_VALUE_2         51 // U8     Calibration value 2
#define ADD_REG_EVT_ENABLE                  52 // U8     Enable the Events
#define ADD_REG_SET_BOARD_TYPE              53 // U8     Type of the board
#define ADD_REG_PROTOCOL_STATE              54 // U8     State of the protocol (running or stopped)
#define ADD_REG_PROTOCOL_DIRECTION          55 // U8     Protocol direction

/************************************************************************/
/* PWM Generator registers' memory limits                               */
/*                                                                      */
/* DON'T change the APP_REGS_ADD_MIN value !!!                          */
/* DON'T change these names !!!                                         */
/************************************************************************/
/* Memory limits */
#define APP_REGS_ADD_MIN                    0x20
#define APP_REGS_ADD_MAX                    0x37
#define APP_NBYTES_OF_REG_BANK              32
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

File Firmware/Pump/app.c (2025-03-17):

#include "hwbp_core.h"
#include "hwbp_core_regs.h"
#include "hwbp_core_types.h"

#include "app.h"
#include "app_funcs.h"
#include "app_ios_and_regs.h"

#define F_CPU 32000000
#include <util/delay.h>

/************************************************************************/
/* Declare application registers                                        */
/************************************************************************/
extern AppRegs app_regs;
extern uint8_t app_regs_type[];
extern uint16_t app_regs_n_elements[];
extern uint8_t *app_regs_pointer[];
extern void (*app_func_rd_pointer[])(void);
extern bool (*app_func_wr_pointer[])(void*);

/************************************************************************/
/* Initialize app                                                       */
/************************************************************************/
static const uint8_t default_device_name[] = "Pump";

void hwbp_app_initialize(void)
{
    /* Define versions */
    uint8_t hwH = 1;
    uint8_t hwL = 1;
    uint8_t fwH = 1;
    uint8_t fwL = 1;
    uint8_t ass = 0;
    
   	/* Start core */
    core_func_start_core(
        1296,
        hwH, hwL,
        fwH, fwL,
        ass,
        (uint8_t*)(&app_regs),
        APP_NBYTES_OF_REG_BANK,
        APP_REGS_ADD_MAX - APP_REGS_ADD_MIN + 1,
        default_device_name,
		false,	// The device is _not_ able to repeat the harp timestamp clock
		false,	// The device is _not_ able to generate the harp timestamp clock
		0		// Default timestamp offset
    );
}

/************************************************************************/
/* Handle if a catastrophic error occur                                 */
/************************************************************************/
void core_callback_catastrophic_error_detected(void)
{
	clr_STEP;
	clr_DIR;
	clr_MS1;
	clr_MS2;
	clr_MS3;
	clr_EN_DRIVER;
	clr_SLEEP;
	clr_RESET;
	
	clr_OUT00;
	clr_OUT01;
	clr_BUF_EN;
}

/************************************************************************/
/* User functions                                                       */
/************************************************************************/
#define DIR_FORWARD 1
#define DIR_REVERSE 0
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

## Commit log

2020-07-28 add initial Firmware project
    [registers.xls]
2020-07-29 init device
2020-08-04 MOTOR_MICROSTEP register handling
2020-08-05 add initial motor handling support
2020-08-05 add basic DIR handling on motor
2020-08-07 update device init
2020-08-07 fix MOTOR_MICROSTEP register handling
2020-08-07 update registers.xls with name, mask fixes and new register
    [registers.xls]
2020-08-17 update registers.xls with protocol variables and start_protocol register
    [registers.xls]
2020-08-20 move DIR pin output change to DIR_STATE register
2020-08-24 enable motor if disabled on STEP
2020-08-26 update step register to guarantee event generation on motor enable
2020-09-07 add support for disabling motor after a period of inactivity
2020-11-06 motor is only turned off on inactivity on microcontroller mode
2020-11-23 [gui] add basic syringe pump view and view model
2020-12-22 [gui] get device name when connecting to device
2020-12-22 [gui] add initial support to save configuration to device
2020-12-29 [gui] add PumpRegisters
2021-01-04 [gui] add device info properties and registers to viewmodel
2021-01-04 [gui] update UI with device information
2021-03-11 [fw] fix initialization on boot while on Arduino mode
2021-03-17 [fw] add new event and board type registers
2021-03-17 [fw] update registers.xls
    [registers.xls]
2021-07-29 [fw] change pin type for arduino mode
2021-08-16 [fw] send DIR event on every change and not depend on enabled motor
2021-11-26 [fw] update registers.xls with Protocol Direction
    [registers.xls]
2022-01-04 Added pump board design files and BOM
    [harp syringe pump v1.1.brd, harp syringe pump v1.1.sch, harp syringe pump v1.1_Bill of Materials.xlsx]
2022-09-01 Squashed commit of the following:
    commit f700bba01e987fa5e4db1dd9f613afa1c31fee5c
    Merge: 5d666ed 6e78613
    Author: Luís Teixeira <micboucinha@gmail.com>
    Date: Fri Feb 4 13:14:21 2022 +0000
    Merge branch 'release/fw0.5'
    commit 6e786132b71c56ce7b7231c306ae5543d8e7abee
    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
    [registers.xls]
2022-09-01 Add CAD files
    [15_SHPHamilton_SYR_5ml_SYP_BLOCK_HOLDER-A.STL, 18_SHPSyPumo_Locker_Plate_to_6ml_Plastic_Syringe.STL, 20_1_x2_SHPSyPump_SideSlider_v2_4-3_mm_to_order.STL, 20_2_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]
2022-09-06 [gui] add MessageBox when a Harp device other than the Pump is connected
2022-09-06 [gui] update target framework
2022-09-22 [gui] move Device.Pump.GUI to its own folder
2022-09-22 [gui] add Device.Pump main project
2022-09-23 [gui] add logs to Device.Pump
2022-09-29 [gui] update flow rate validation
2022-09-29 [gui] small update on loading device information
2022-09-30 [gui] update connection and initial loading of device information
2023-03-15 [gui] move starting of app to the supporting assembly
2023-03-15 [gui] add missing DeviceConfiguration class
2023-03-15 [gui] handle connections to other devices
2023-03-30 [gui] remove Bluetooth devices from list on Mac
2023-04-12 Add assembly instructions
2023-04-12 Restructure repository
    [15_SHPHamilton_SYR_5ml_SYP_BLOCK_HOLDER-A.STL, 18_SHPSyPumo_Locker_Plate_to_6ml_Plastic_Syringe.STL, 20_1_x2_SHPSyPump_SideSlider_v2_4-3_mm_to_order.STL, 20_2_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]
2023-04-12 Add first version of device schema
2023-04-19 Add PCB image
2023-04-24 Change assembly prefix
2023-04-25 Update Device classes to latest schema
2023-06-10 Update schema for consistency across devices
2023-06-10 Update `Device` classes to new schema
2023-06-12 Update WhoAmI in the `Device` class
2023-06-22 Update device id and firmware version
2023-06-22 Update App to allow the new device ID and old one
2023-06-29 update registers - remove aux notes
    [registers.xls]
2024-11-13 Update device schema source
